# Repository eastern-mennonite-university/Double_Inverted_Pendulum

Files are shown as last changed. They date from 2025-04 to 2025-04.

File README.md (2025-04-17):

## Project Overview

The main constraint of this project was to build the inverted pendulum system at a total cost of $500, while creating a robust system that will continue to be used for future control system classes and research. After calculating system accuracy requirements, mechanical and electrical components were found to match the specifications. A full CAD (Computer Aided Design) assembly was modeled using Solidworks (Figure 2) and engineering drawings created for individual parts. The subsections of the system are the steel base, linear guide system, motor and belt drive, pendulum arms and pivots, and electronics and sensors. After procuring materials and components, the individual components were manufactured using 3D printing, machining, and welding. The final design allows for the system to be used as a single and double inverted pendulum.

### Youtube Video of working single inverted pendulum

Watch on YouTube (https://www.youtube.com/watch?v=rqrJa7szEt4)

## Control System

A framework for an Arduino based PID controller was developed using ChatGPT, with separate PIDs for each controlled motion. PID controller outputs, encoder angles and time were collected to create graphs for tuning purposes. The encoders are calibrated by aligning the arms in a vertical position with the Arduino reading and storing the position. Safety limits are programmed that if a cart position or angle threshold is exceeded, the motor is disabled.

## PID Tuning

The controller that balances the first beam was tuned using Ziegler Nichols method. This was done by increasing the proportional constant until the system reached continuous oscillation, with the period of oscillation and required proportional constant then used to calculate values for P, I and D. In order to tune the PID controller that centers the cart, the graphs of system and controller data were analyzed to determine values for P, I and D. The proportional constant was increased until the system responded quickly to error. The derivative constant was added to remove overshoot, and a small amount of integral was added to reduce steady state error.

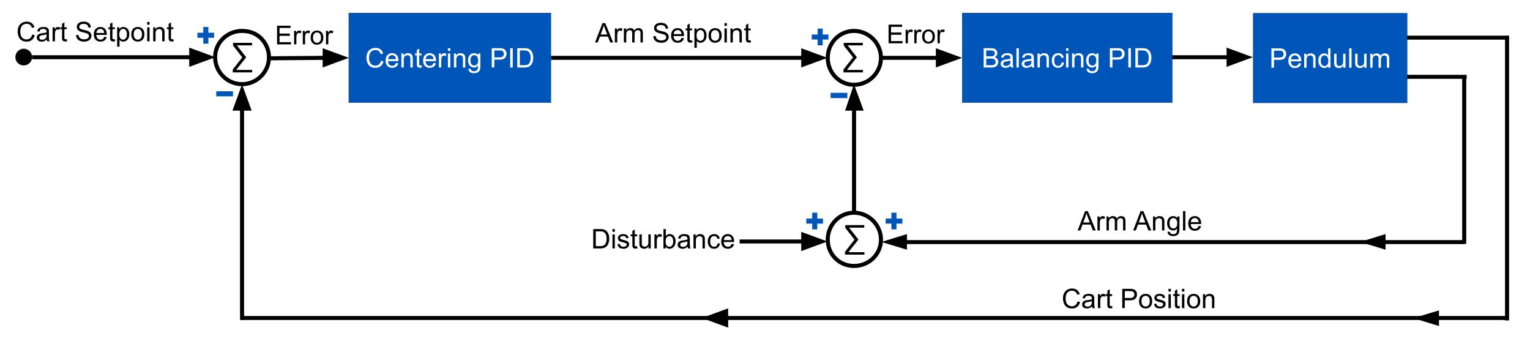
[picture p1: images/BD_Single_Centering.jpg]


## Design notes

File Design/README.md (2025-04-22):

## Design

All parts designed for the pendulum were first modeled in SolidWorks and put in an assembly to assure accurate design. Purchased parts were either modeled as well or models were found online to be included in the assembly.

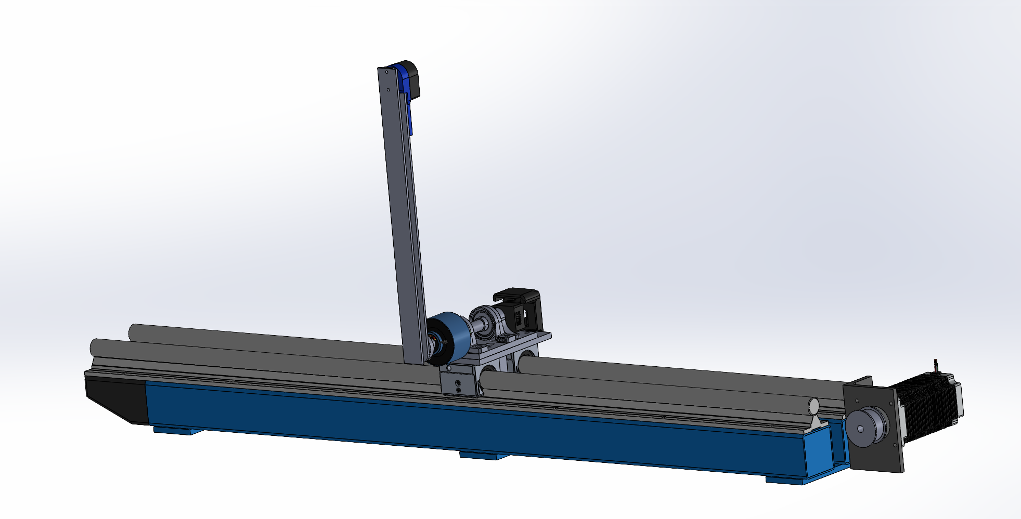
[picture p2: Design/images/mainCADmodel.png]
Main CAD Model


The project budget was roughly $500. Including estimated raw materials, the total bill of materials is shown here. The total amount we spent was just under $400, and the estimated total including parts we had was roughly $550.

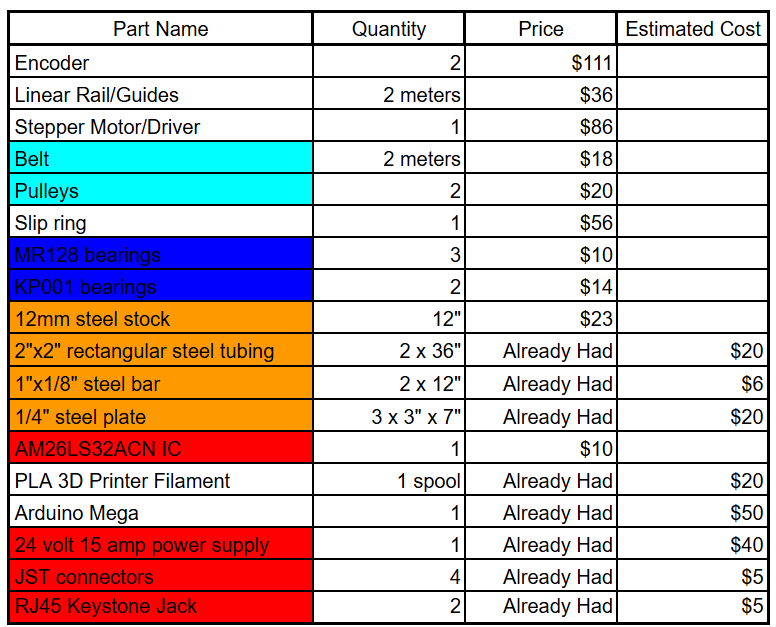
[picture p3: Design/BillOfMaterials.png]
Bill of Materials


> **Note:** All CAD files were created with a student license of SolidWorks.

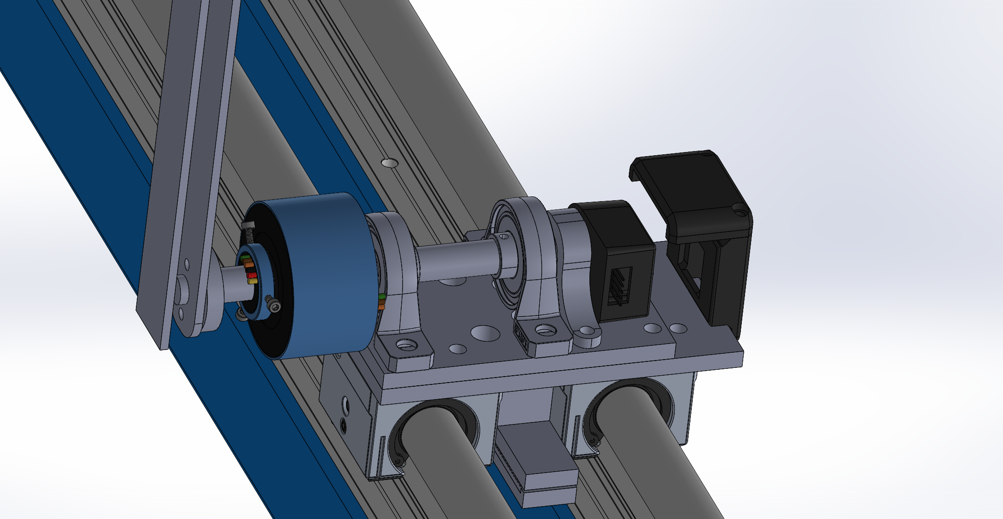
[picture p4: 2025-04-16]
Design/images/Screenshot 2025-04-16 164635.png

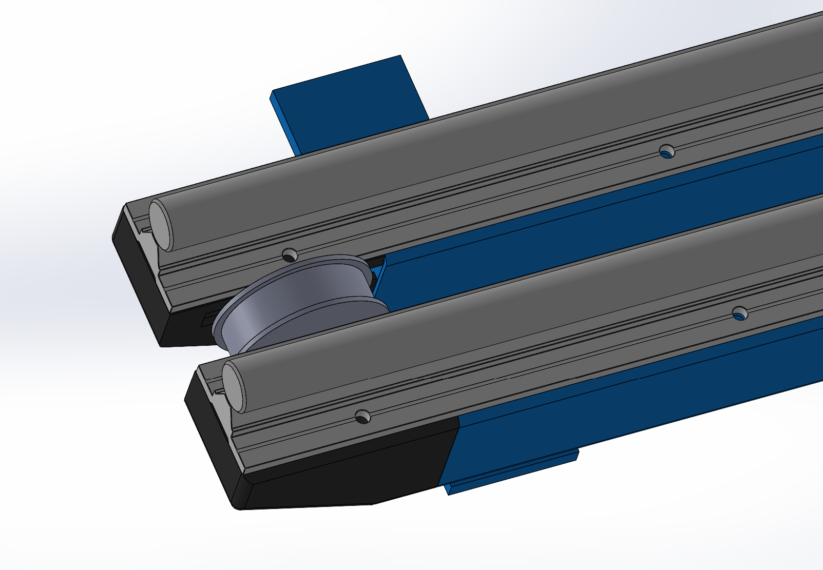
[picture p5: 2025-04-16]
Design/images/Screenshot 2025-04-16 164704.png

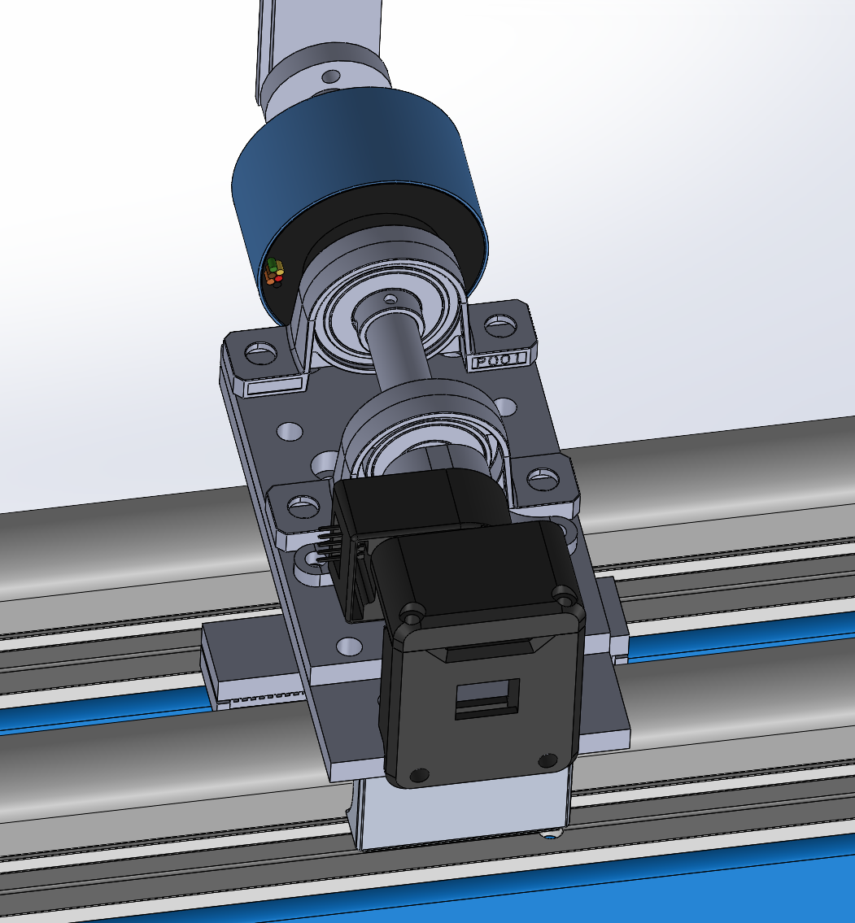
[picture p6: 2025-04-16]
Design/images/Screenshot 2025-04-16 164845.png

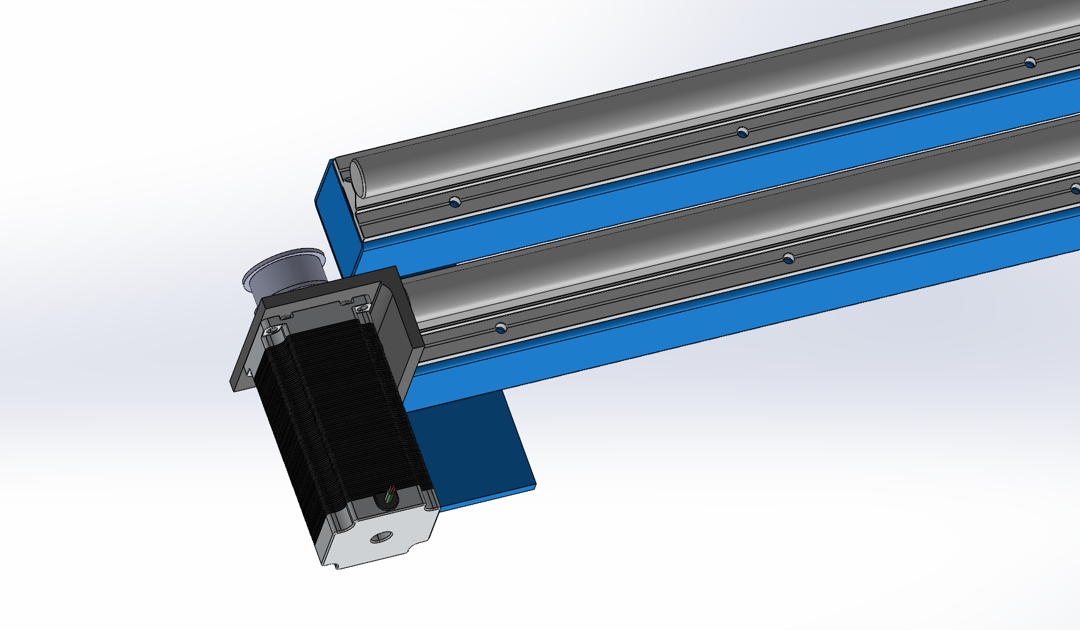
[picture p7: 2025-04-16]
Design/images/Screenshot 2025-04-16 164731.png

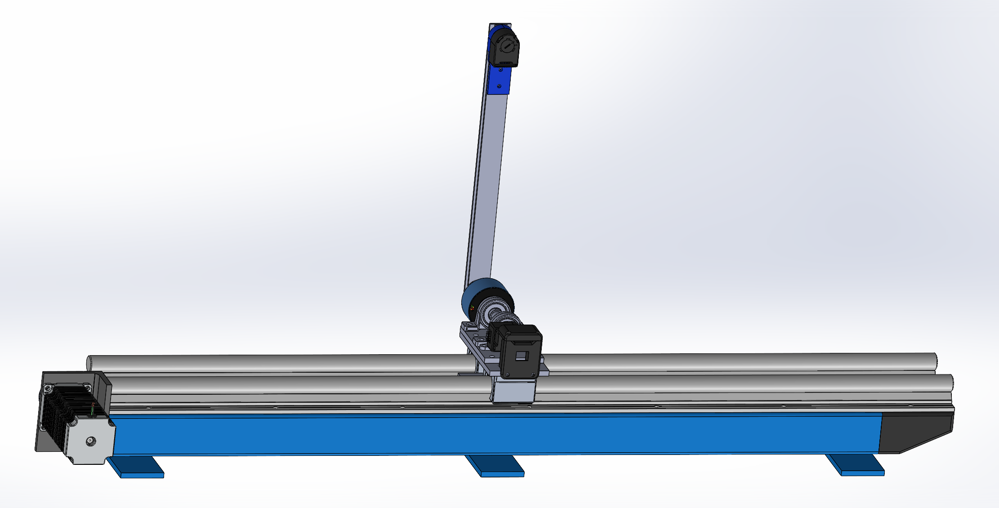
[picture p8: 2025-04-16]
Design/images/Screenshot 2025-04-16 164811.png

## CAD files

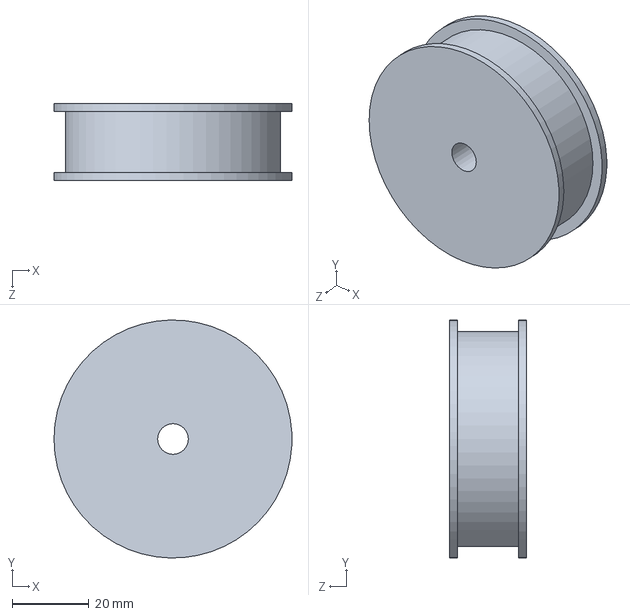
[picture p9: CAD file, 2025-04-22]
Design/CAD/Idler_Pulley.SLDPRT
62.0 x 62.0 x 20.0 mm

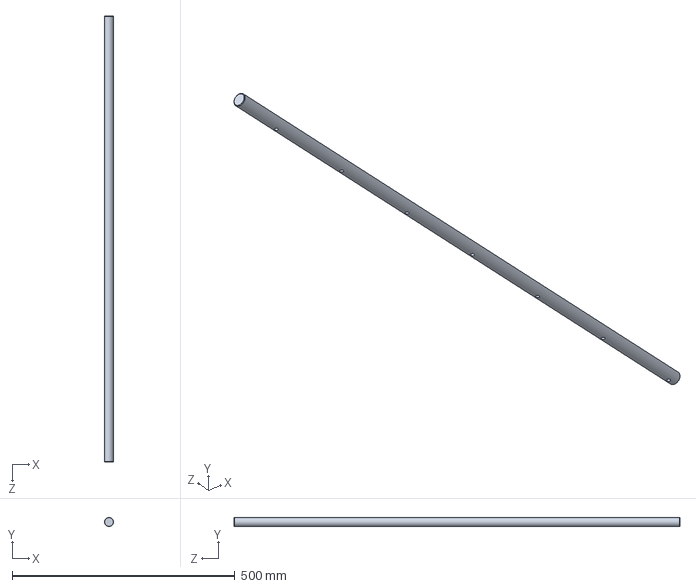
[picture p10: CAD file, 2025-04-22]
Design/CAD/BR20-1.SLDPRT
20.0 x 20.0 x 1000.0 mm

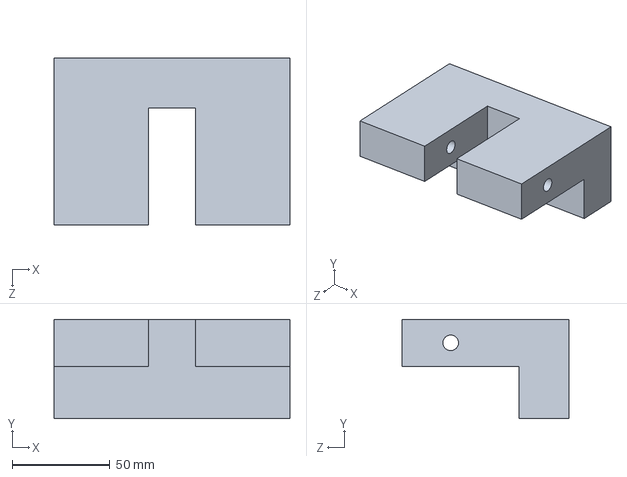
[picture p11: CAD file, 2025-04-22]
Design/CAD/Tensioner_Mount.SLDPRT
120.8 x 50.8 x 85.6 mm

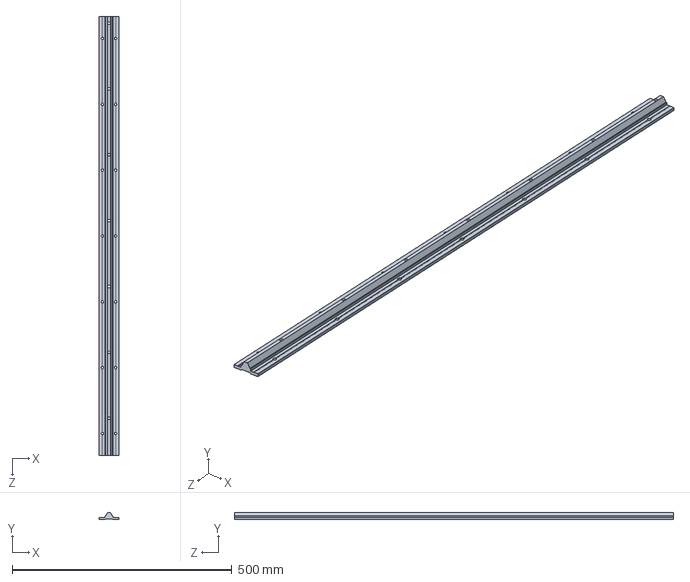
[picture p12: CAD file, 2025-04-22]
Design/CAD/BR20-2.SLDPRT
45.0 x 17.0 x 1000.0 mm

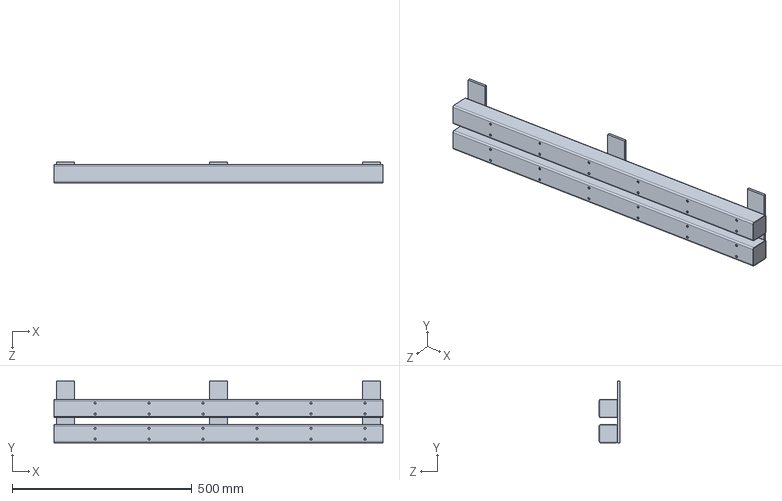
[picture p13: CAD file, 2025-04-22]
Design/CAD/Inverted_Pendulum_Base.SLDPRT
914.4 x 171.6 x 57.2 mm

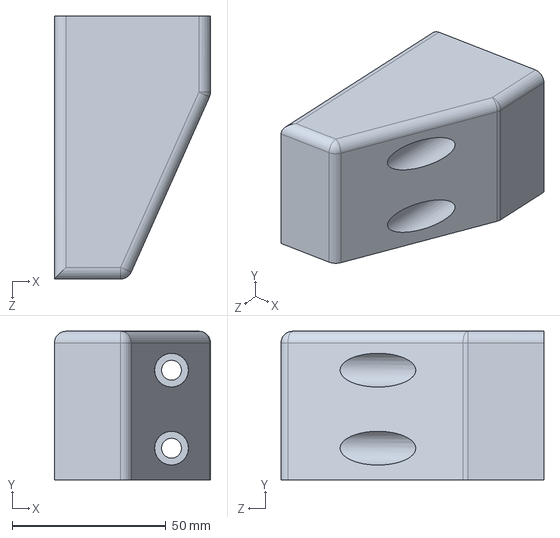
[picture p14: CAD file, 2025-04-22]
Design/CAD/IdlerMount.SLDPRT
50.8 x 48.4 x 85.6 mm

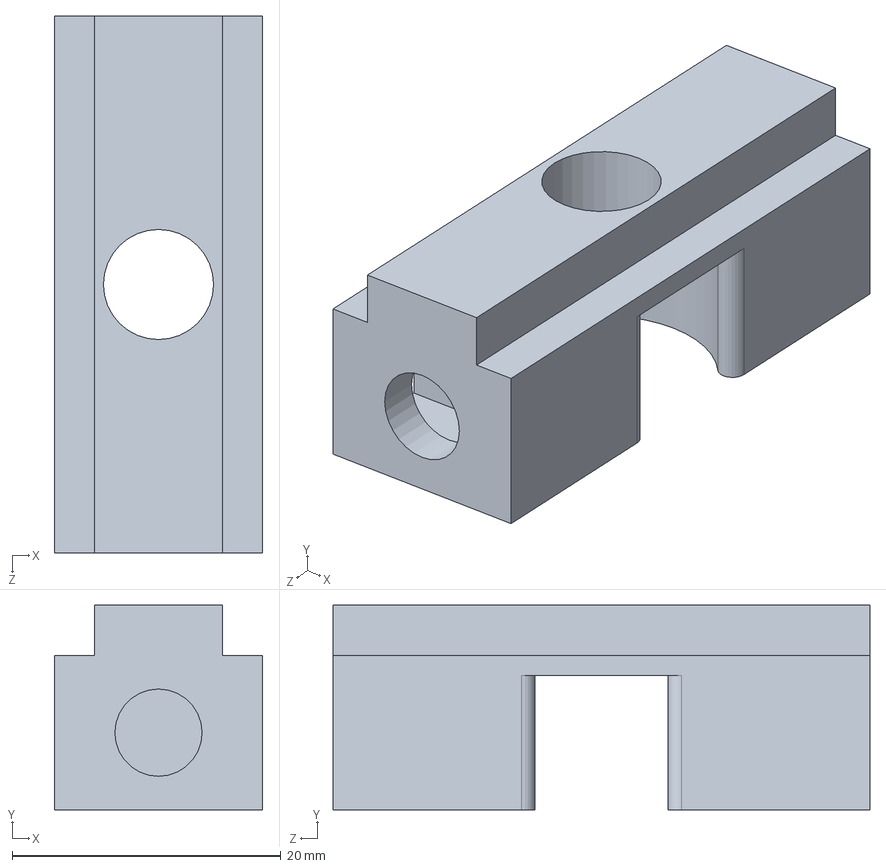
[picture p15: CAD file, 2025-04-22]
Design/CAD/Bolt_Side_Idler_Slide.SLDPRT
15.5 x 15.2 x 40.0 mm

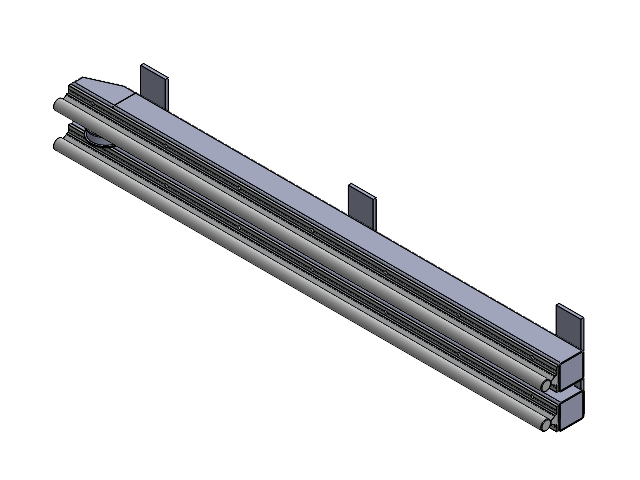
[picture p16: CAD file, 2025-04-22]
Design/CAD/Main_Assembly.SLDASM
Inverted Pendulum Base
BR20-2 x 2
BR20-1 x 2
Idler Mount
Bolt Side Idler Slide
Idler Pulley
Nut Side Idler Slide
MirrorIdler Mount

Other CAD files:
Design/CAD/Profile1.SLDPRT
Design/CAD/MirrorIdler Mount.SLDPRT
Design/CAD/Nut_Side_Idler_Slide.SLDPRT

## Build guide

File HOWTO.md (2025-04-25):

## Steps for Simple Operation

### Setup:
1. Plug in Stepper Motor and Stepper Encoder cables (Encoder has two plugs, one to Stepper Driver and one for Arduino)  
2. Plug in a Cat6 (Ethernet) cable to the Control and Power Unit and the Pendulum Cart  
3. Plug in a C13 cable into the Control and Power Unit  
4. Ensure Emergency Stop Button is plugged into GND and pin 52 (unplugged will cause fault)  
5. Power Arduino using USB-B cable or compatible barrel plug  

### Operation:
1. Place the cart in the center (line up the two black lines on the front)  
2. Let the pendulum arm hang down freely  
3. Flip on Power Switch on Control and Power Unit  
4. Once red light on Arduino turns off, flip pendulum arm vertical  
5. Once arm is 180 degrees from its hanging position, the balancing control will activate  

### On Fault:  
(*If angle > 15 degrees, position exceeds safe limits, or Emergency Stop Button is pressed*)  
1. Cart will return to center automatically  
2. Let the pendulum arm hang down freely  
3. Once red light on Arduino turns off, flip pendulum arm vertical  
4. Once arm is 180 degrees from its hanging position, the balancing control will activate  

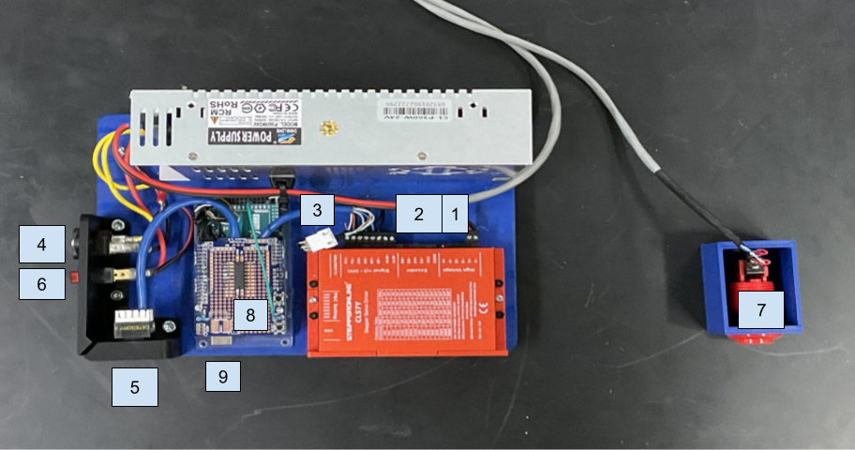
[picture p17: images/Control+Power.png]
Control and Power Unit


### Important Locations:
1. Motor connector  
2. Motor Encoder connector (only for Stepper Driver)  
3. Motor Encoder connector #2 (connects to Arduino)  
4. C14 connector (receiver for C13 cable)  
5. Ethernet port for communication with pendulum  
6. Main Power Switch  
7. Emergency Kill Button  
8. Red LED on Arduino  
9. USB-B for reprogramming

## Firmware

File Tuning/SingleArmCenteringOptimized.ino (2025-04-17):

#include <PID_v2.h>
#include <TimerOne.h>

// Stop Button
int stopButtonPin = 52;
int buttonState = 0;

// Encoder pins
const uint8_t ENCODER_A = 2;  // Interrupt pin for pendulum encoder
const uint8_t ENCODER_B = 3;  // Digital pin for pendulum encoder
const uint8_t CART_ENCODER_A = 18;  // Interrupt pin for cart position
const uint8_t CART_ENCODER_B = 19;  // Digital pin for cart position

// Stepper motor control pins
const uint8_t STEP_PIN = 10;
const uint8_t DIR_PIN = 11;
const uint8_t MF_PIN = 12;
const uint8_t LED = 44;

// Time tracking
unsigned long startTime = millis();
unsigned long timeElapsed;
bool failstate = false;

// Encoder position tracking
volatile long rawPendulumPosition = 0;
volatile long rawCartPosition = 0;
double cartPosition = 0;
double maxOffset = 12;

// Pendulum Control PID
double angle = 0, setpoint = 0, pendulumOutput = 0, toperror = 0;
const double Kp = 4, Ki = 66, Kd = 0;
PID pendulumPID(&toperror, &pendulumOutput, &setpoint, Kp, Ki, Kd, DIRECT);

// Cart Position Control PID
double cartSetpoint = 0, cartOutput = 0;
//const double Kp_cart = 2.0, Ki_cart = 20, Kd_cart = 5;  // Adjust based on tuning
const double Kp_cart = 1.6, Ki_cart = 1.0, Kd_cart = 2.3;
PID cartPID(&cartPosition, &cartOutput, &cartSetpoint, Kp_cart, Ki_cart, Kd_cart, DIRECT);

// Stepper parameters
const int MAX_STEP_SPEED = 8000;  // Max step rate

// Stepper movement setup
volatile long stepsRemaining = 0;
volatile bool stepState = false;
volatile bool isStepping = false;


// Helper to calculate total movement time
unsigned long getStepDurationMicros(long steps, long intervalMicros) {
  return abs(steps) * 2L * intervalMicros; // 2 toggles per step
}

//Changing cart position
int state = 1; //starts at zero
int positions[4] = {-200, 0, 200, 0};



void setup() {
    Serial.begin(115200);
    

    // Stop Button setup
    pinMode(stopButtonPin, INPUT_PULLUP);

    // Pendulum encoder setup
    pinMode(ENCODER_A, INPUT_PULLUP);
    pinMode(ENCODER_B, INPUT_PULLUP);
    attachInterrupt(digitalPinToInterrupt(ENCODER_A), encoderISR, CHANGE);
    attachInterrupt(digitalPinToInterrupt(ENCODER_B), encoderISR, CHANGE);

    // Cart pendulum encoder setup
    pinMode(CART_ENCODER_A, INPUT_PULLUP);
    pinMode(CART_ENCODER_B, INPUT_PULLUP);
    attachInterrupt(digitalPinToInterrupt(CART_ENCODER_A), cartEncoderISR, CHANGE);
    attachInterrupt(digitalPinToInterrupt(CART_ENCODER_B), cartEncoderISR, CHANGE);
    
    // Stepper setup
    pinMode(STEP_PIN, OUTPUT);
    pinMode(DIR_PIN, OUTPUT);
    pinMode(MF_PIN, OUTPUT);
    pinMode(LED, OUTPUT);

    //digitalWrite(MF_PIN, HIGH); // Disables motor

    // PID setup
    pendulumPID.SetMode(AUTOMATIC);
    pendulumPID.SetOutputLimits(-8000, 8000); // Range of PID output for pendulum
    pendulumPID.SetSampleTime(10);

    cartPID.SetMode(AUTOMATIC);
    cartPID.SetOutputLimits(-1000, 1000);  // Range of PID output for cart
    cartPID.SetSampleTime(10);

    Timer1.initialize(100);  // Dummy value, will be updated when stepping starts
    Timer1.attachInterrupt(stepperISR);  // ISR that toggles STEP pin
    Timer1.stop();  // Don't run until commanded

    //initialization();
    //digitalWrite(MF_PIN, LOW); // Enables Motor

    delay(1000); // Initial delay before running
    rawCartPosition = 0;
    swingup();


}

void loop() {

  while (failstate == false) {

      buttonState = digitalRead(stopButtonPin); // Reads EM stop button
      balance();
      serialprint();
      delay(1); // Removes a some oscillation

     if(abs(angle) > 15 || abs(cartPosition) > 325 || buttonState == 1) { // Checks all three failstates, max angle, max position and EM button
        failstate = true;
        digitalWrite(MF_PIN, HIGH);
        digitalWrite(LED, HIGH);
        delay(1000);
        swingup(); // Runs swingup to reset pendulum
      }
    
  }

}

void balance() {

    // Compute angle from pendulum encoder position
    angle = rawPendulumPosition * .045;  // Second value is Degrees/Pulse = 360 / 8000 (8000 = pendulum encoder resolution)
    toperror = sin(angle*3.14159/180)*320; // Calculates strait line distance error using trig

    // Compute cart distance from cart encoder position
    cartPosition = rawCartPosition * .03; // Second value is mm/pulse = 120 / 4000 (120 = circumference of motor pulley, 4000 = motor encoder resolution)

    // Run PID controllers
    cartPID.Compute();

    setpoint = cartOutput * -maxOffset / 1000; // Calculate Angle PID setpoint based on Cart PID output

    pendulumPID.Compute();
    
    // Get elapsed time for data analysis purposes
    timeElapsed = millis() - startTime;

    // Move stepper motor
    startStepping(pendulumOutput, 10); // Moves set distance at a fixed speed

}


void swingup() { 
  delay(500);
  cartPosition = rawCartPosition * .03;

  // Moves cart to center
  while (abs(cartPosition) > 2) {
    cartPosition = rawCartPosition * .03;
    startStepping(-rawCartPosition, 100);
  }

  double oldangle = 0; // Used for finding if the pendulum is still swinging
  angle = rawPendulumPosition * .045;

  // Waits for pendlum to stop swinging
  while (oldangle != angle) {
    oldangle = angle;
    delay(1000);
    angle = rawPendulumPosition * .045;
  }
  rawPendulumPosition = 4000; // Once determined pendulum is still, resets position to 180 degrees
  // Serial.println("angle set to 180");

  while (angle > 1 || angle < -1) { // Waits for pendulum to be brought back to the top
    delay(10);
    angle = rawPendulumPosition * .045;
    if (angle > 359 && angle < 361) {
      rawPendulumPosition = 0 + (angle-360)*(8000/360); // Resets angle to zero if rotated the wrong way
    }
    // Serial.print(angle);
    // Serial.print(", ");
    // Serial.println("wating... ");
    digitalWrite(LED, LOW);

      }
  failstate = false; // resets failstate

}

void changingSetpoint() {
  if ((timeElapsed % 10000 <= 2) && timeElapsed > 1000) {
    Serial.println("setpoint changed to " + positions[state]);
    state = state + 1;
    if  (state == 4) {
      state = 0;
    }
    cartSetpoint = positions[state];
  }
}

void serialprint() {
    // Print data
    Serial.print(timeElapsed);
    Serial.print(",");
    Serial.print(setpoint);
    Serial.print(",");
    Serial.print(angle);
    Serial.print(",");
    Serial.print(pendulumOutput);
    Serial.print(",");
    Serial.print(cartPosition);
    Serial.print(",");
    Serial.println(cartOutput);
}

// Call this to begin a move
void startStepping(long numberOfSteps, long intervalMicros) {
  digitalWrite(DIR_PIN, numberOfSteps < 0 ? HIGH : LOW);
  stepsRemaining = abs(numberOfSteps) * 2; // 2 toggles per full step (HIGH + LOW)
  Timer1.setPeriod(intervalMicros);
  Timer1.start();
}

void moveStepper(double speed) {
    digitalWrite(DIR_PIN, speed < 0 ? HIGH : LOW);
    
    speed = abs(speed);
    for (int i = 0; i < speed; i++) {
        digitalWrite(STEP_PIN, HIGH);
        delayMicroseconds(1);
        digitalWrite(STEP_PIN, LOW);
        delayMicroseconds(1);
    }
}

// This gets called automatically at each step interval
void stepperISR() {
  if (stepsRemaining > 0) {
    digitalWrite(STEP_PIN, stepState);
    stepState = !stepState;
    stepsRemaining--;
  } else {
    Timer1.stop();
    digitalWrite(STEP_PIN, LOW);
    stepState = false;
  }
}

void initialization() {
  // User calibration prompt for pendulum angle
    Serial.println("Let the pendulum hang down and press Enter to calibrate ANGLE to 180.");
    while (!Serial.available()) {}
    Serial.read();
    rawPendulumPosition = 4000;
    Serial.println("Pendulum angle calibrated!");

    // User calibration prompt for cart position
    Serial.println("Press Enter to calibrate the CART position to 0.");
    while (!Serial.available()) {}
    Serial.read();
    rawCartPosition = 0;
    Serial.println("Cart position calibrated!");
}

// Interrupt Service Routine for pendulum quadrature decoding

void encoderISR() {
  static uint8_t last = 0;
  uint8_t a = (PINE & (1 << 4)) ? 1 : 0;  // Read pin 2 (PE4)
  uint8_t b = (PINE & (1 << 5)) ? 1 : 0;  // Read pin 3 (PE5)
  uint8_t current = (a << 1) | b;

  uint8_t transition = (last << 2) | current;

  if (transition == 1 || transition == 7 || transition == 14 || transition == 8) {
    rawPendulumPosition++;
  } else if (transition == 2 || transition == 4 || transition == 13 || transition == 11) {
    rawPendulumPosition--;
  }

  last = current;
}

void cartEncoderISR() {
  static uint8_t last = 0;
  uint8_t a = (PIND & (1 << PD2)) ? 1 : 0;  // Read CART_ENCODER_A (e.g. pin D2)
  uint8_t b = (PIND & (1 << PD3)) ? 1 : 0;  // Read CART_ENCODER_B (e.g. pin D3)
  uint8_t current = (a << 1) | b;

  uint8_t transition = (last << 2) | current;

  if (transition == 1 || transition == 7 || transition == 14 || transition == 8) {
    rawCartPosition--;
  } else if (transition == 2 || transition == 4 || transition == 13 || transition == 11) {
    rawCartPosition++;
  }

  last = current;
}

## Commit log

2025-04-16 Rename Bill Of Materials.png to BillOfMaterials.png
2025-04-17 Main Arduino code
2025-04-22 Rename Design/Idler Mount.SLDPRT to Design/CAD/IdlerMount.SLDPRT
    [IdlerMount.SLDPRT]
